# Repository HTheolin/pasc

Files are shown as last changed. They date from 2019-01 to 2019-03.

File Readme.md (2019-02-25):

# Användbara länkar

## Rust
svd2rust - https://docs.rs/svd2rust/0.14.0/svd2rust/  \
Rustboken - https://doc.rust-lang.org/1.4.0/book/README.html  \
Embedde rust - https://rust-embedded.github.io/book/intro/index.html  \
CubeMX och Rust - http://www.hashmismatch.net/pragmatic-bare-metal-rust/

## Hårdvara
STM32F401RE datasheet - https://www.st.com/resource/en/datasheet/stm32f401re.pdf

## Dokument
High Level specification - https://docs.google.com/document/d/1pT679ALJbP6M4RAu0LiHIDUVMe5iSUqeqp4-EVYOUyA/edit# \
Komponenter - https://docs.google.com/spreadsheets/d/1eK-V_FMpTHM5hmX8ijiI2q-JYo_6xdile7O38F0DbRs/edit#gid=0

# High Level Specification
Hälsoarmband som mäter puls och steg med pulsmätare och accelerometer.
Knapp som startar och återställer stegräknare. Strömspar som stänger display, sänker sampling frekvens, ... ev. efter lång tid utan knapptryck.
## Purpose (what problem it solves)
Mäta puls och känna av om pulsen blir låg/hög, varna vid dessa.
## Limitations (what problem(s) it cannot solve)
Visar endast realtid puls, yttre temperatur och steg, inget minne. Larmar endast närmaste omgivningen. 
## Behaviour (how the problem is solved)
Genom att mäta puls med en sensor en gång per sek, om den blir låg eller hög starta larm med högtalare. Visar data på display. Återställer data och startar genom knapptryck. Med detta system skapas en tryggare värld.

## Safety (what it must not do, e.g., electrocute the user)
Eftersom systemet är designat att vara i kontakt med person, måste tåla viss mängd fukt och inte ge elektiska stötar till användaren.
## Liveness (what it must eventually do, e.g., process data) 
Måste visa puls minst var 10e sekund under batteritid. 
## Robustness (how it should react to non-expected input, e.g., mal-formed packages)
Om ingen puls stäng system. 

# Gradings
## Grade 3
Pulse measurements from analog in. \
Timer that's set using buttons. \
Buzzer that sounds alarm when high pulse or timer reaching zero. \
USART for serial communication with com.
## Grade 4
Temperature measurements using analog in. \
Output to display using SPI \
Low power mode
## Grade 5
Accelerometer detecting steps, using accelerometer values or tap interrupts over I2C. \
Menu for selecting output to display and other settings.

# Group division
All - STM 32 init, Soldering \
August - ADC, Buttons, Display Layouts \
Simon - USART, Display \
Ridge - Timer, Piezo \
Henrik - Display, Acccelerometer

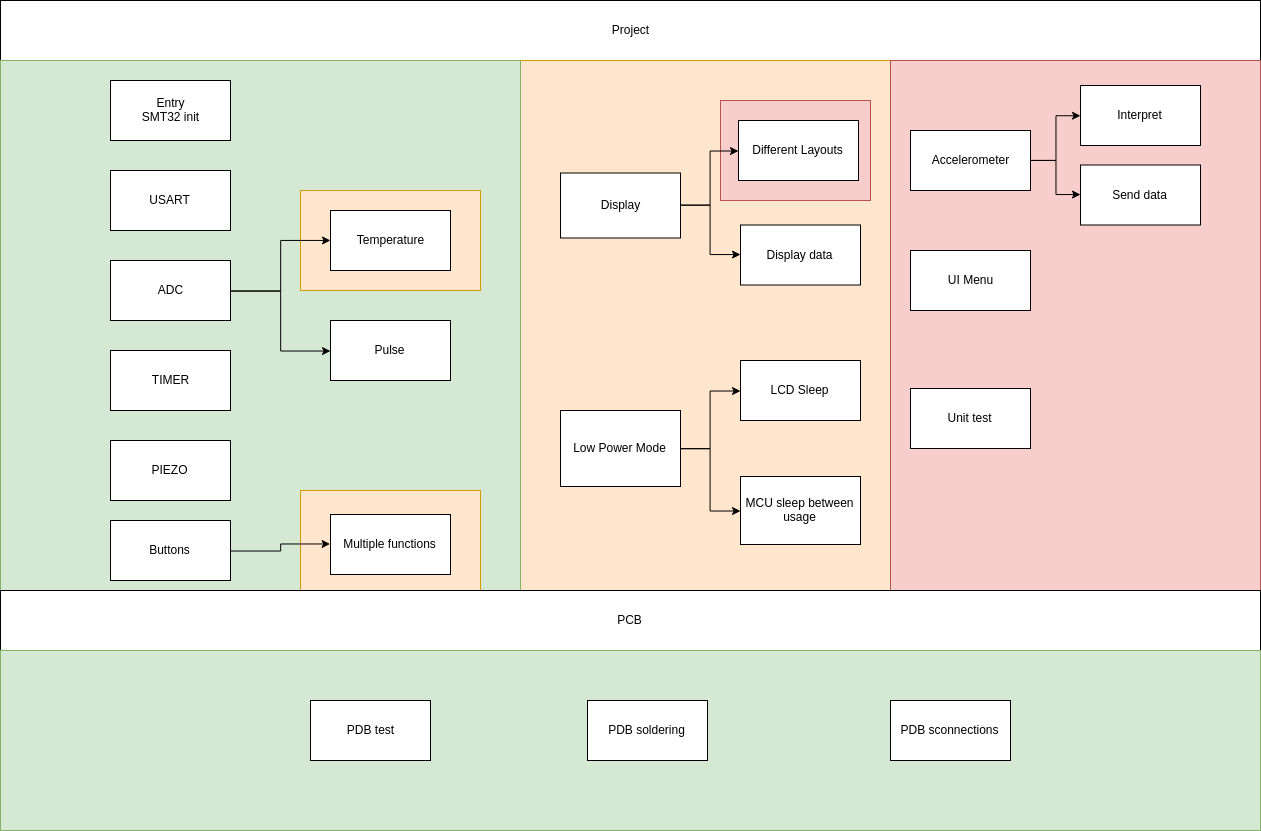
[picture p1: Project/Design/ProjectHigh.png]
System design


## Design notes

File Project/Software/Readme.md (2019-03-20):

# PASC software

## How To: Debug/Program

```
$ cargo build
$ openocd -f openocd.cfg
```

```
$ arm-none-eabi-gdb target/thumbv7em-none-eabihf/debug/Software -x openocd.gdb
```

## Difference between boards:
Layout differences between boards:

### Schematic_ons
```
    Button U9  -> MCU pin 26 (PB0)
    Button U10 -> MCU pin 27 (PB1)
    Button U11 -> MCU pin 28 (PB2)
```
LCD:
```
        3: LCD_SCE -> MCU pin 8 (PC0)
        4: LCD_RST -> MCU pin 9 (PC1)
        5: LCD_DC -> MCU pin 10 (PC2)
        6: SPI1_MOSI -> MCU pin 23 (PA7)
        7: SPI1_SCK -> MCU pin 21 (PA5)
        8: LED -> MCU pin 22 (PA6)
```

### Schematic_Ubuntu
```
    Button U9  -> MCU pin 38 (PC7)
    Button U10 -> MCU pin 39 (PC8)
    Button U11 -> MCU pin 40 (PC9)
```
LCD:
```
        3: LCD_SCE -> MCU pin 25 (PC5)
        4: LCD_RST -> MCU pin 24 (PC4)
        5: LCD_DC -> MCU pin 26 (PB0)
        6: SPI1_MOSI -> MCU pin 23 (PA7, set to SPI1_MOSI, AF05)
        7: SPI1_SCK -> MCU pin 21 (PA5, set to SPI1_SK, AF05)
        8: LED -> MCU pin 37 (PC6, set to TIM3_CH1, AF02)
```

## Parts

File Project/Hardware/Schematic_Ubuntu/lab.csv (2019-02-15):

Id | Designator | Package | Quantity | Designation | Supplier and ref
1 | SW1 | SPDT-100 | 1 | SW_SPDT
2 | U6 | Nokia5110 | 1 | Nokia5110
3 | U5 | SO-8_5.3x6.2mm_Pitch1.27mm | 1 | MAX4460ESA+
4 | BT1 | Pin_Header_Straight_1x02_Pitch2.54mm | 1 | Battery
5 | C1,C4 | CP_Radial_D5.0mm_P2.00mm | 2 | 10u
6 | C2,C3,C5,C10,C11,C12,C13,C14,C16,C17,C18 | C_0805_HandSoldering | 11 | 100n
7 | C6,C7 | C_0805_HandSoldering | 2 | 18p
8 | C8,C9 | C_0805_HandSoldering | 2 | 4.7u
9 | C15,C19 | C_0805_HandSoldering | 2 | 1u
10 | D1 | D_DO-35_SOD27_P7.62mm_Horizontal | 1 | 1N4148
11 | J1 | USB_Micro_B_Female_10118193-0001LF | 1 | USB_B_Micro
12 | J2 | Pin_Header_Straight_1x06_Pitch2.54mm | 1 | 6P Male
13 | J3 | Pin_Header_Straight_1x03_Pitch2.54mm | 1 | Conn_01x03_Male
14 | Q1 | TO-92_Inline_Wide | 1 | 2N3904
15 | R1,R2 | R_0805_HandSoldering | 2 | 10k
16 | R3,R4 | R_0805_HandSoldering | 2 | 8.2k
17 | R5,R6 | R_0805_HandSoldering | 2 | 270k
18 | R7,R13,R14,R15,R16,R17,R18 | R_0805_HandSoldering | 7 | 1k
19 | R8 | R_0805_HandSoldering | 1 | 1.8k
20 | R9,R19 | R_0805_HandSoldering | 2 | 100k
21 | R10 | R_0805_HandSoldering | 1 | 2.7k
22 | R11 | R_0805_HandSoldering | 1 | 820
23 | R12 | R_0805_HandSoldering | 1 | 330
24 | TH1 | TO-92-2pin_Inline_Narrow_Oval | 1 | PT1000
25 | U1 | SOT-223-3_TabPin2 | 1 | NCP1117-3.3_SOT223
26 | U2 | LQFP-64_10x10mm_Pitch0.5mm | 1 | STM32F411RETx
27 | U3 | LIS3DH | 1 | lis3dh_board
28 | U4 | Pin_Header_Straight_1x03_Pitch2.54mm | 1 | Pulse_sensor
29 | U7 | Piezo | 1 | piezo
30 | U8,U9,U10,U11 | Momentswitch | 4 | MomentSwitch
31 | Y1 | Crystal_SMD_HC49-SD_HandSoldering | 1 | 8MHz
32 | C20,C21,C22 | C_0805_HandSoldering | 3 | C

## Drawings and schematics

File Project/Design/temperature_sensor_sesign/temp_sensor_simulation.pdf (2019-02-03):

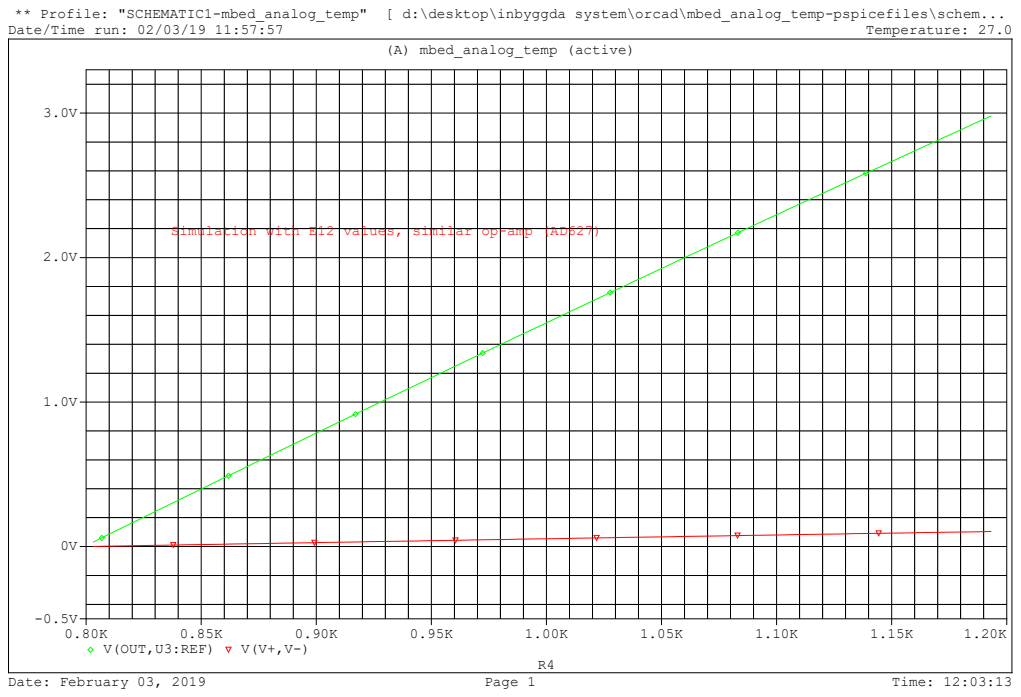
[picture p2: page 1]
Temperature: 27.0; Date: February 03, 2019; Page 1; Time: 12:03:13; (A) mbed_analog_temp (active); V(OUT,U3:REF); Simulation with E12; values,; similar; op-amp (AD627)

** Profile: "SCHEMATIC1-mbed_analog_temp" [ d:\desktop\inbyggda system\orcad\mbed_analog_temp-pspicefiles\schem...
Date/Time run: 02/03/19 11:57:57

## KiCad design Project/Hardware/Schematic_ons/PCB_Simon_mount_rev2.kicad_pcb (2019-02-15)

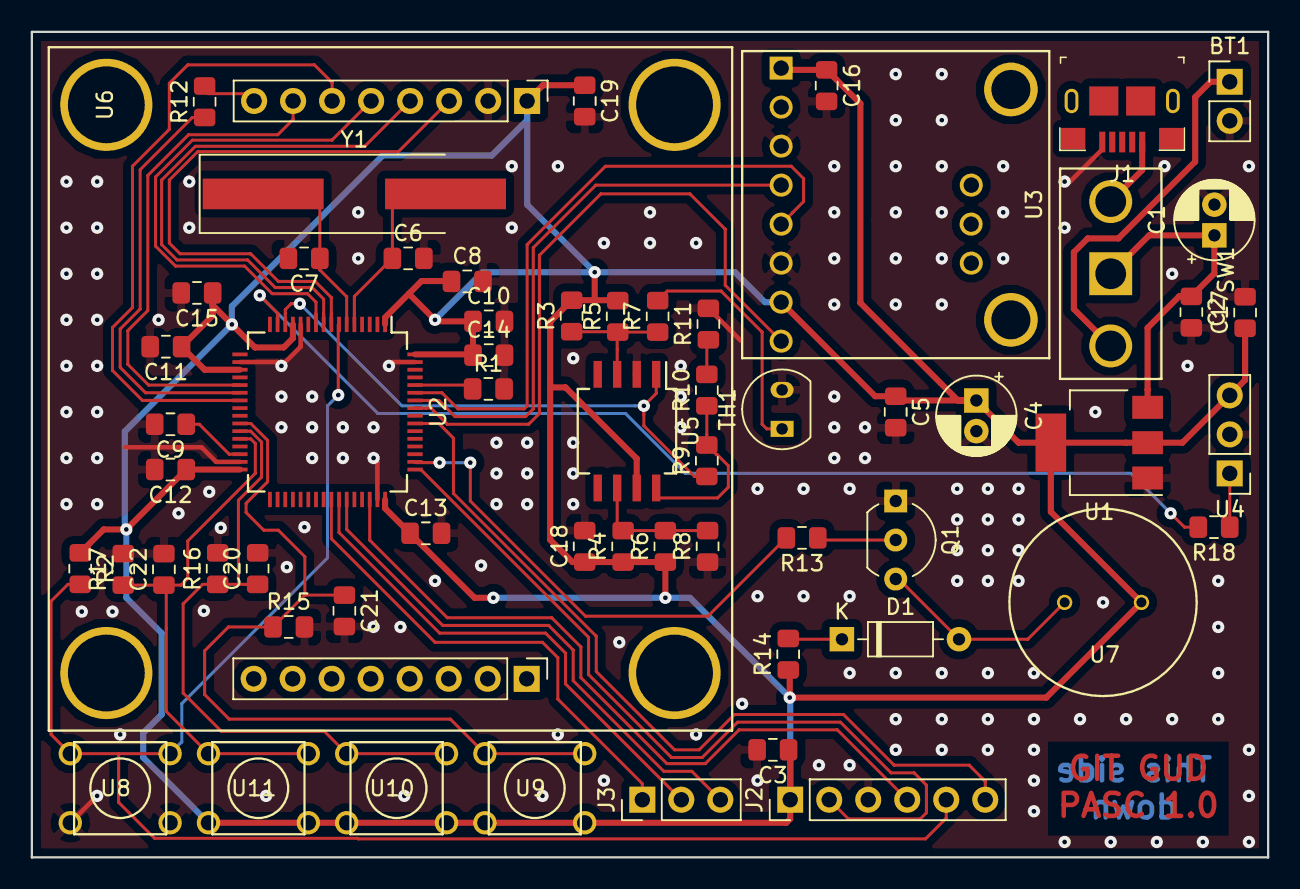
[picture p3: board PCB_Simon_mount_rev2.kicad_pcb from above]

Board: 2 copper layers, 80.5 x 53.8 mm, 60 parts (0 on the bottom side), 41 nets.

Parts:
BT1: Battery; PinHeader_1x02_P2.54mm_Vertical
C1, C4: 10u; CP_Radial_D5.0mm_P2.00mm
C2, C3, C5, C10, C11, C12, C13, C14, C16, C17, C18, C20, C21, C22: 100n; C_0805_2012Metric_Pad1.15x1.40mm_HandSolder
C6, C7: 18p; C_0805_2012Metric_Pad1.15x1.40mm_HandSolder
C8, C9: 4.7u; C_0805_2012Metric_Pad1.15x1.40mm_HandSolder
C15, C19: 1u; C_0805_2012Metric_Pad1.15x1.40mm_HandSolder
D1: 1N4148; D_DO-35_SOD27_P7.62mm_Horizontal
J1: USB_B_Micro; USB_Micro_B_Female_10118193-0001LF
J2: 6P Male; PinHeader_1x06_P2.54mm_Vertical
J3: Conn_01x03_Male; PinHeader_1x03_P2.54mm_Vertical
Q1: 2N3904; TO-92_Inline_Wide
R1, R2: 10k; R_0805_2012Metric_Pad1.15x1.40mm_HandSolder
R3, R4: 8.2k; R_0805_2012Metric_Pad1.15x1.40mm_HandSolder
R5, R6: 270k; R_0805_2012Metric_Pad1.15x1.40mm_HandSolder
R7, R13, R14, R15, R16, R17, R18: 1k; R_0805_2012Metric_Pad1.15x1.40mm_HandSolder
R8: 1.8k; R_0805_2012Metric_Pad1.15x1.40mm_HandSolder
R9: 100k; R_0805_2012Metric_Pad1.15x1.40mm_HandSolder
R10: 2.7k; R_0805_2012Metric_Pad1.15x1.40mm_HandSolder
R11: 820; R_0805_2012Metric_Pad1.15x1.40mm_HandSolder
R12: 330; R_0805_2012Metric_Pad1.15x1.40mm_HandSolder
SW1: SW_SPDT; SPDT-100
TH1: PT1000; TO-92-2
U1: NCP1117-3.3_SOT223; SOT-223-3_TabPin2
U2: STM32F411RETx; LQFP-64_10x10mm_P0.5mm
U3: lis3dh_board; LIS3DH
U4: Pulse_sensor; PinHeader_1x03_P2.54mm_Vertical
U5: MAX4460ESA+; SO-8_5.3x6.2mm_P1.27mm
U6: Nokia5110
U7: piezo; Piezo
U8, U9, U10, U11: MomentSwitch; Momentswitch
Y1: 8MHz; Crystal_SMD_HC49-SD_HandSoldering

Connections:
+3V3: C3.1, C4.1, C5.1, C8.1, C10.1, C11.1, C12.1, C13.1, C14.1, C15.1, C16.1, C17.1, C18.1, C19.1, J2.1, R2.1, R3.2, R4.1, R5.2, R6.1, R14.1, U1.2, U2.1, U2.13, U2.19, U2.32, U2.48, U2.64, U3.1, U3.7, U4.3, U5.7, U6.1, U7.1, U9.1, U9.2, U10.1, U10.2, U11.1, U11.2
+5V: J1.1, SW1.3
+BATT: BT1.1, SW1.1
+VIN: C1.1, C2.1, SW1.2, U1.3
/CS_INT: U2.57, U3.8
/Display/LED: R12.2, U6.8
/I2C1_SCL: U2.58, U3.4
/I2C1_SDA: U2.59, U3.5
/LCD_DC: U2.10, U6.5
/LCD_RST: U2.9, U6.4
/LCD_SCE: U2.8, U6.3
/NRST: J2.5, R2.2, U2.7, U8.3, U8.4
/PIEZOPWM: R13.2, U2.50
/PULSESIG: R18.2, U2.15
/SPI1_MOSI: U2.23, U6.6
/SPI1_SCK: U2.21, U6.7
/SWCLK: J2.2, U2.49
/SWDIO: J2.4, U2.46
/SWO: J2.6, U2.55
/TEMPOUT: R9.1, U2.14, U5.1
/TIM3_CH1: R12.1, U2.22
/TIM_INC: C20.1, R16.1, U2.27, U10.3, U10.4
/TIM_RES: C22.1, R17.1, U2.28, U11.3, U11.4
/TIM_START: C21.1, R15.1, U2.26, U9.3, U9.4
/Temp Sensor/INAMPFB: R9.2, R10.1, U5.8
/Temp Sensor/WBRIDGE+: R3.1, R5.1, R7.1, U5.3
/Temp Sensor/WBRIDGE-: R4.2, R6.2, R8.2, U5.6
/USART1_CK: J3.1, U2.41
/USART1_RX: J3.3, U2.43
/USART1_TX: J3.2, U2.42
/XTAL+: C6.1, U2.5, Y1.2
/XTAL-: C7.1, U2.6, Y1.1
GND: BT1.2, C1.2, C2.2, C3.2, C4.2, C5.2, C6.2, C7.2, C8.2, C9.2, C10.2, C11.2, C12.2, C13.2, C14.2, C15.2, C16.2, C17.2, C18.2, C19.2, C20.2, C21.2, C22.2, J1.5, J2.3, Q1.1, R1.2, R8.1, R11.2, R15.2, R16.2, R17.2, TH1.2, U1.1, U2.12, U2.18, U2.31, U2.47, U2.63, U3.3, U3.6, U4.2, U5.2, U6.2, U8.1, U8.2
unnamed: C9.1, U2.30
unnamed: D1.1, R14.2
unnamed: D1.2, Q1.3, U7.2
unnamed: Q1.2, R13.1
unnamed: R1.1, U2.60
unnamed: R7.2, TH1.1
unnamed: R10.2, R11.1
unnamed: R18.1, U4.1

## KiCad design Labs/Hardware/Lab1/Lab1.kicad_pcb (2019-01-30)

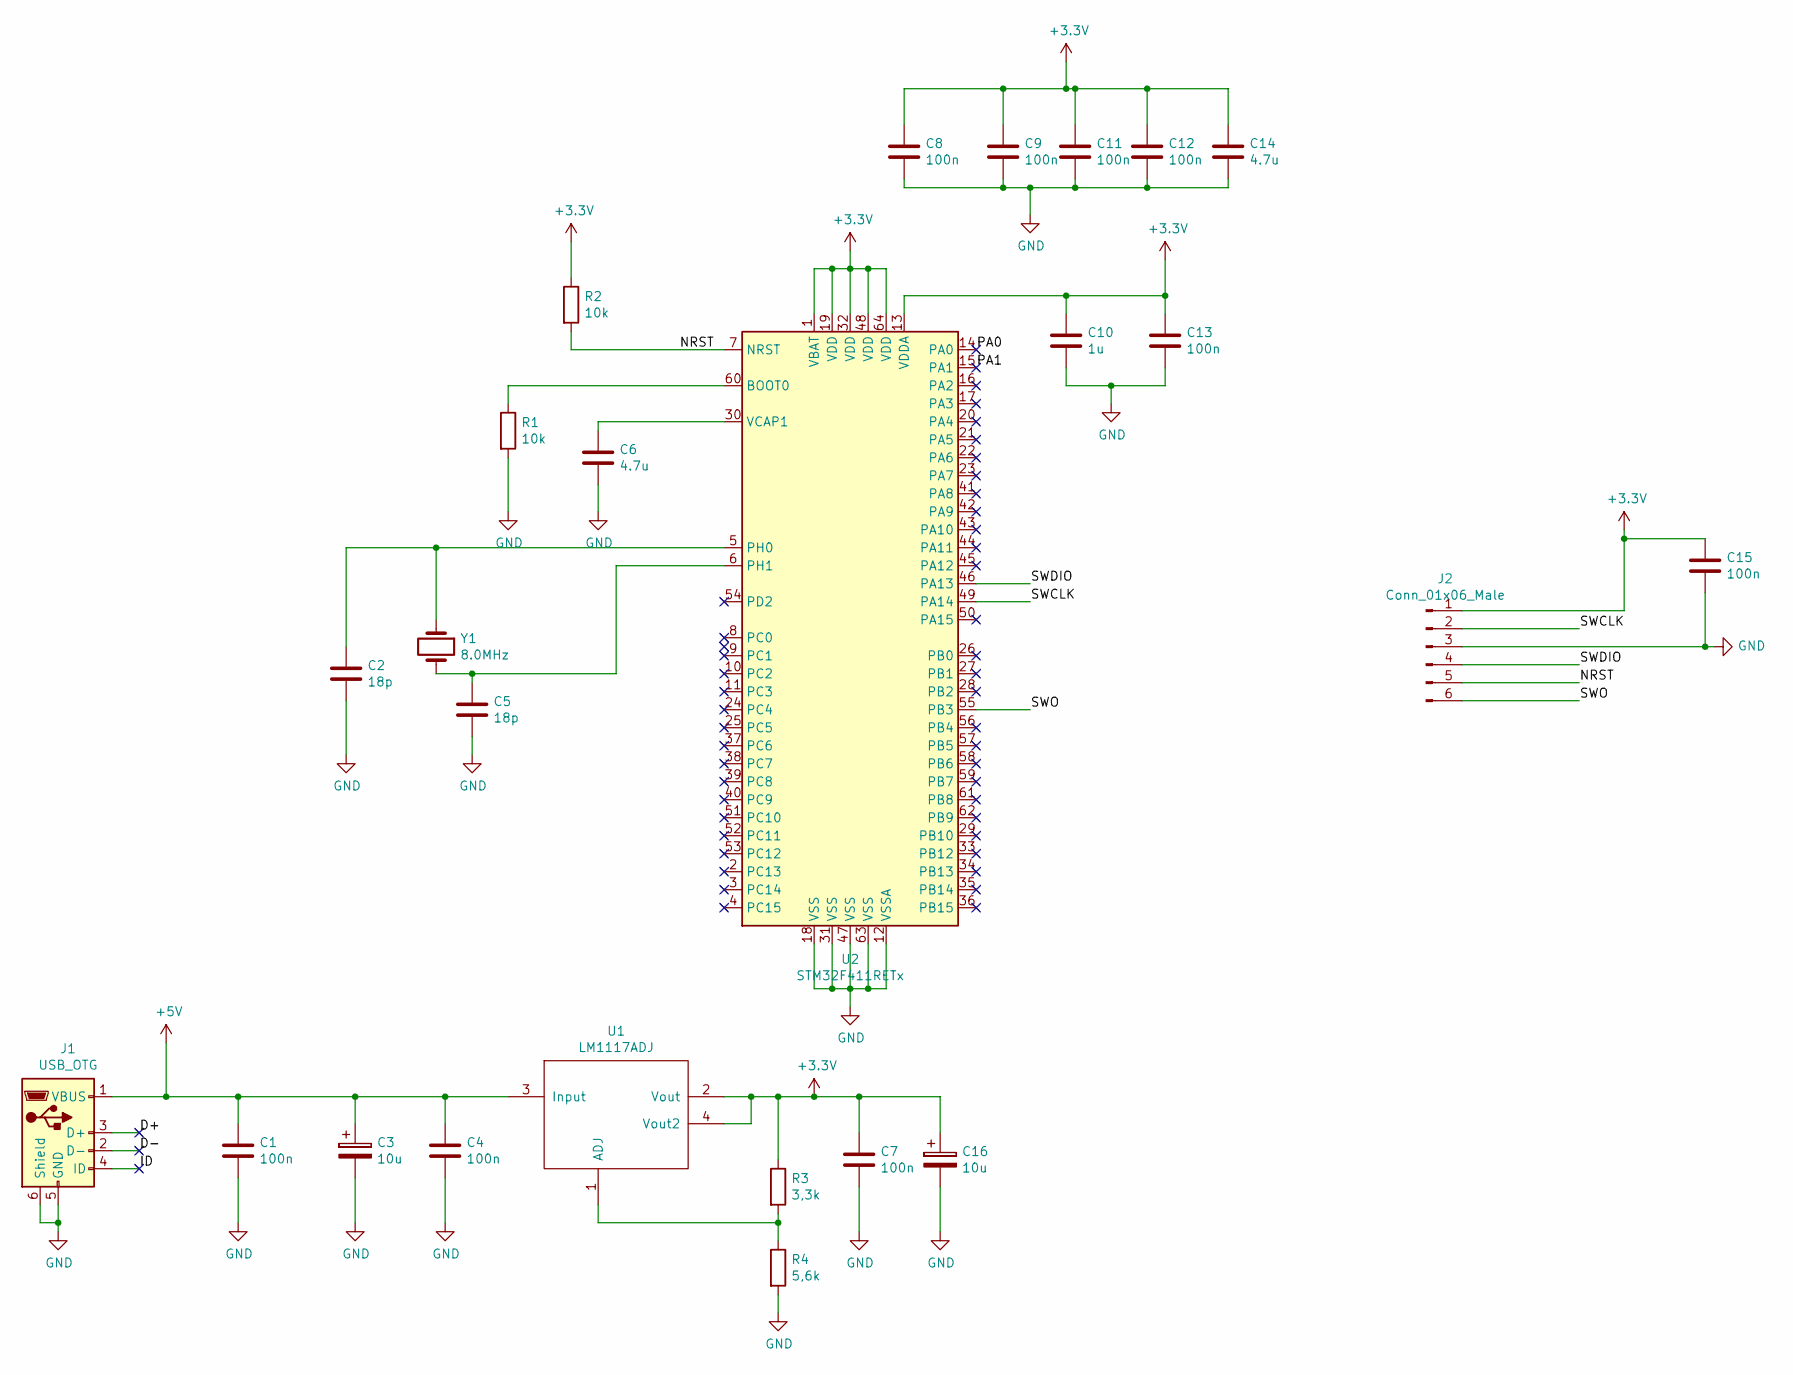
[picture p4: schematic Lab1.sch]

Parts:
C1, C4, C7, C8, C9, C11, C12, C13, C15: 100n; C_0805_HandSoldering
C2, C5: 18p; C_0805_HandSoldering
C3, C16: 10u; CP_Elec_5x5.3
C6, C14: 4.7u; C_0805_HandSoldering
C10: 1u; C_0805_HandSoldering
J1: USB_OTG; USB_Mini-B_AdamTech_MUSB-B5-S-VT-TSMT-1_SMD_Vertical
J2: Conn_01x06_Male; Pin_Header_Straight_1x06_Pitch2.54mm
R1, R2: 10k; R_0805_HandSoldering
R3: 3,3k; R_0805_HandSoldering
R4: 5,6k; R_0805_HandSoldering
U1: LM1117ADJ; SOT-223
U2: STM32F411RETx; LQFP-64_10x10mm_Pitch0.5mm
Y1: 8.0MHz; Crystal_SMD_HC49-SD_HandSoldering

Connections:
+3V3: C7.1, C8.1, C9.1, C10.1, C11.1, C12.1, C13.1, C14.1, C15.1, C16.1, J2.1, R2.1, R3.1, U1.2 (Vout), U1.4 (Vout2), U2.1 (VBAT), U2.13 (VDDA), U2.19 (VDD), U2.32 (VDD), U2.48 (VDD), U2.64 (VDD)
+5V: C1.1, C3.1, C4.1, J1.1 (VBUS), U1.3 (Input)
/D+: J1.3 (D+)
/D-: J1.2 (D-)
/ID: J1.4 (ID)
/NRST: J2.5, R2.2, U2.7 (NRST)
/PA0: U2.14 (PA0)
/PA1: U2.15 (PA1)
/SWCLK: J2.2, U2.49 (PA14)
/SWDIO: J2.4, U2.46 (PA13)
/SWO: J2.6, U2.55 (PB3)
GND: C1.2, C2.2, C3.2, C4.2, C5.2, C6.2, C7.2, C8.2, C9.2, C10.2, C11.2, C12.2, C13.2, C14.2, C15.2, C16.2, J1.5 (GND), J1.6 (Shield), J2.3, R1.2, R4.2, U2.12 (VSSA), U2.18 (VSS), U2.31 (VSS), U2.47 (VSS), U2.63 (VSS)
unnamed: C2.1, U2.5 (PH0), Y1.1
unnamed: C5.1, U2.6 (PH1), Y1.2
unnamed: C6.1, U2.30 (VCAP1)
unnamed: R1.1, U2.60 (BOOT0)
unnamed: R3.2, R4.1, U1.1 (ADJ)

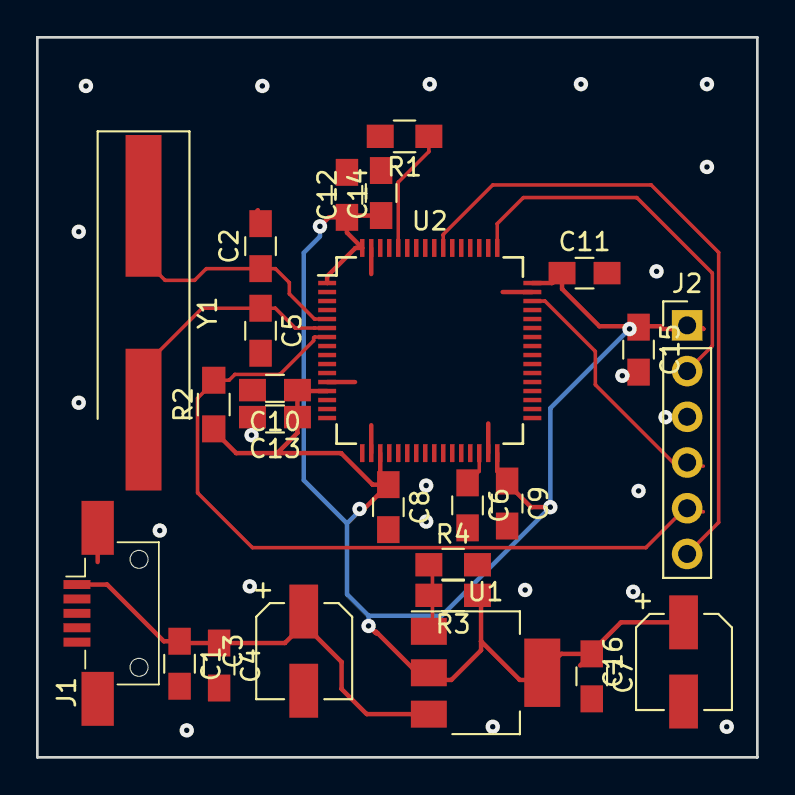
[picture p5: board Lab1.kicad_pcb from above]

Board: 2 copper layers, 40.0 x 40.0 mm, 25 parts (0 on the bottom side), 12 nets.

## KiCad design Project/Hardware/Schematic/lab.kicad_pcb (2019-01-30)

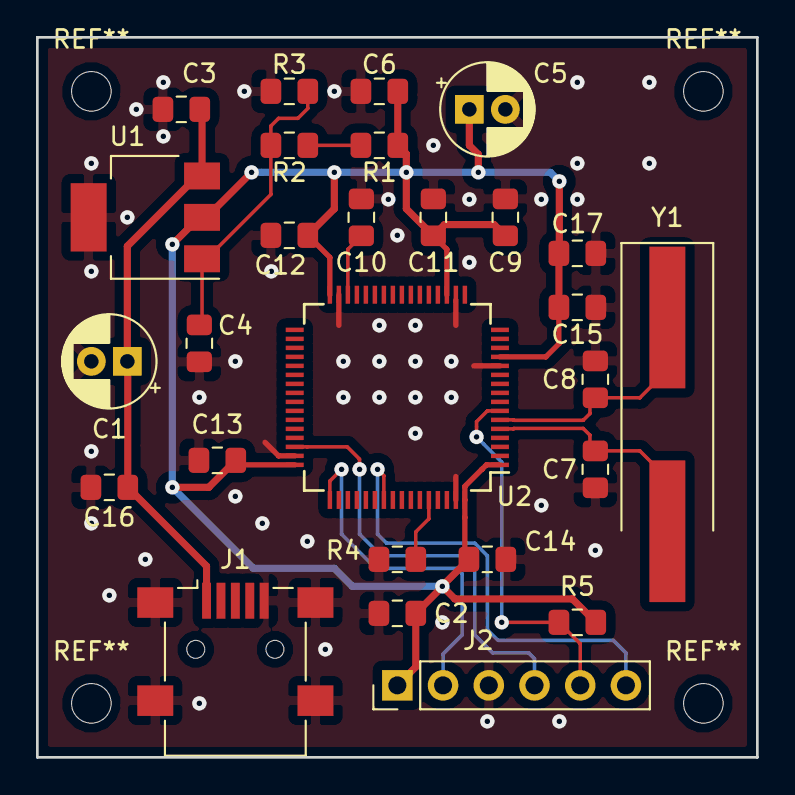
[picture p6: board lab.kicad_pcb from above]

Board: 2 copper layers, 40.0 x 40.0 mm, 27 parts (0 on the bottom side), 13 nets.

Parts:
C1, C5: 10u; CP_Radial_D5.0mm_P2.00mm
C2, C3, C4, C6, C11, C12, C13, C14, C15, C16: 100n; C_0805_2012Metric_Pad1.15x1.40mm_HandSolder
C7, C8: 18p; C_0805_2012Metric_Pad1.15x1.40mm_HandSolder
C9, C10: 4.7u; C_0805_2012Metric_Pad1.15x1.40mm_HandSolder
C17: 1u; C_0805_2012Metric_Pad1.15x1.40mm_HandSolder
J1: USB_OTG; USB_Mini-B_Lumberg_2486_01_Horizontal
J2: 6P Male; PinHeader_1x06_P2.54mm_Vertical
R1: 2.2k; R_0805_2012Metric_Pad1.15x1.40mm_HandSolder
R2: 3.9k; R_0805_2012Metric_Pad1.15x1.40mm_HandSolder
R3, R4, R5: 10k; R_0805_2012Metric_Pad1.15x1.40mm_HandSolder
U1: LM1117ADJ; SOT-223
U2: STM32F411RETx; LQFP-64_10x10mm_P0.5mm
Y1: 8MHz; Crystal_SMD_HC49-SD_HandSoldering

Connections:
+3V3: C2.1, C5.1, C6.1, C9.1, C11.1, C12.1, C13.1, C14.1, C15.1, C17.1, J2.1, R1.1, R5.1, U1.2, U2.1, U2.13, U2.19, U2.32, U2.48, U2.64
+5V: C1.1, C3.1, C16.1, J1.1, U1.3
/NRST: J2.5, R5.2, U2.7
/SWCLK: J2.2, U2.49
/SWDIO: J2.4, U2.46
/SWO: J2.6, U2.55
/XTAL+: C7.1, U2.5, Y1.2
/XTAL-: C8.1, U2.6, Y1.1
GND: C1.2, C2.2, C3.2, C4.2, C5.2, C6.2, C7.2, C8.2, C9.2, C10.2, C11.2, C12.2, C13.2, C14.2, C15.2, C16.2, C17.2, J1.5, J1.6, J2.3, R3.2, R4.2, U1.4, U2.12, U2.18, U2.31, U2.47, U2.63
unnamed: C4.1, R2.2, R3.1, U1.1
unnamed: C10.1, U2.30
unnamed: R1.2, R2.1
unnamed: R4.1, U2.60

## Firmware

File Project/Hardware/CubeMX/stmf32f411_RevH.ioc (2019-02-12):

#MicroXplorer Configuration settings - do not modify
ADC1.Channel-0\#ChannelRegularConversion=ADC_CHANNEL_1
ADC1.IPParameters=Rank-0\#ChannelRegularConversion,Channel-0\#ChannelRegularConversion,SamplingTime-0\#ChannelRegularConversion,NbrOfConversionFlag,master
ADC1.NbrOfConversionFlag=1
ADC1.Rank-0\#ChannelRegularConversion=1
ADC1.SamplingTime-0\#ChannelRegularConversion=ADC_SAMPLETIME_3CYCLES
ADC1.master=1
File.Version=6
KeepUserPlacement=false
Mcu.Family=STM32F4
Mcu.IP0=ADC1
Mcu.IP1=I2C1
Mcu.IP2=NVIC
Mcu.IP3=RCC
Mcu.IP4=SPI1
Mcu.IP5=SYS
Mcu.IP6=TIM2
Mcu.IP7=TIM3
Mcu.IP8=USART1
Mcu.IPNb=9
Mcu.Name=STM32F411R(C-E)Tx
Mcu.Package=LQFP64
Mcu.Pin0=PC0
Mcu.Pin1=PC1
Mcu.Pin10=PA10
Mcu.Pin11=PA13
Mcu.Pin12=PA14
Mcu.Pin13=PA15
Mcu.Pin14=PC10
Mcu.Pin15=PC11
Mcu.Pin16=PB3
Mcu.Pin17=PB5
Mcu.Pin18=PB6
Mcu.Pin19=PB7
Mcu.Pin2=PC2
Mcu.Pin20=VP_SYS_VS_Systick
Mcu.Pin21=VP_TIM2_VS_ClockSourceINT
Mcu.Pin3=PA0-WKUP
Mcu.Pin4=PA1
Mcu.Pin5=PA5
Mcu.Pin6=PA6
Mcu.Pin7=PA7
Mcu.Pin8=PA8
Mcu.Pin9=PA9
Mcu.PinsNb=22
Mcu.ThirdPartyNb=0
Mcu.UserConstants=
Mcu.UserName=STM32F411RETx
MxCube.Version=4.24.0
MxDb.Version=DB.4.0.240
NVIC.BusFault_IRQn=true\:0\:0\:false\:false\:true\:false
NVIC.DebugMonitor_IRQn=true\:0\:0\:false\:false\:true\:false
NVIC.HardFault_IRQn=true\:0\:0\:false\:false\:true\:false
NVIC.MemoryManagement_IRQn=true\:0\:0\:false\:false\:true\:false
NVIC.NonMaskableInt_IRQn=true\:0\:0\:false\:false\:true\:false
NVIC.PendSV_IRQn=true\:0\:0\:false\:false\:true\:false
NVIC.PriorityGroup=NVIC_PRIORITYGROUP_4
NVIC.SVCall_IRQn=true\:0\:0\:false\:false\:true\:false
NVIC.SysTick_IRQn=true\:0\:0\:false\:false\:true\:false
NVIC.UsageFault_IRQn=true\:0\:0\:false\:false\:true\:false
PA0-WKUP.Signal=ADCx_IN0
PA1.Signal=ADCx_IN1
PA10.Mode=Synchronous
PA10.Signal=USART1_RX
PA13.Locked=true
PA13.Signal=SYS_JTMS-SWDIO
PA14.Locked=true
PA14.Signal=SYS_JTCK-SWCLK
PA15.Signal=S_TIM2_CH1_ETR
PA5.Mode=Simplex_Bidirectional_Master
PA5.Signal=SPI1_SCK
PA6.Signal=S_TIM3_CH1
PA7.Mode=Simplex_Bidirectional_Master
PA7.Signal=SPI1_MOSI
PA8.Mode=Synchronous
PA8.Signal=USART1_CK
PA9.Mode=Synchronous
PA9.Signal=USART1_TX
PB3.Locked=true
PB3.Signal=SYS_JTDO-SWO
PB5.Locked=true
PB5.Signal=GPXTI5
PB6.Mode=I2C
PB6.Signal=I2C1_SCL
PB7.Mode=I2C
PB7.Signal=I2C1_SDA
PC0.Locked=true
PC0.Signal=GPIO_Output
PC1.Locked=true
PC1.Signal=GPIO_Output
PC10.Locked=true
PC10.Signal=GPIO_Output
PC11.Locked=true
PC11.Signal=GPIO_Output
PC2.Locked=true
PC2.Signal=GPIO_Output
PCC.Checker=false
PCC.Line=STM32F411
PCC.MCU=STM32F411R(C-E)Tx
PCC.PartNumber=STM32F411RETx
PCC.Seq0=0
PCC.Series=STM32F4
PCC.Temperature=25
PCC.Vdd=null
PinOutPanel.RotationAngle=0
RCC.AHBFreq_Value=16000000
RCC.APB1Freq_Value=16000000
RCC.APB2Freq_Value=16000000
RCC.CortexFreq_Value=16000000
RCC.FamilyName=M
RCC.HSE_VALUE=25000000
RCC.HSI_VALUE=16000000
RCC.I2SClocksFreq_Value=96000000
RCC.IPParameters=AHBFreq_Value,APB1Freq_Value,APB2Freq_Value,CortexFreq_Value,FamilyName,HSE_VALUE,HSI_VALUE,I2SClocksFreq_Value,LSE_VALUE,LSI_VALUE,PLLCLKFreq_Value,PLLQCLKFreq_Value,RTCFreq_Value,RTCHSEDivFreq_Value,SYSCLKFreq_VALUE,VCOI2SOutputFreq_Value,VCOInputFreq_Value,VCOInputMFreq_Value,VCOOutputFreq_Value,VcooutputI2S
RCC.LSE_VALUE=32768
RCC.LSI_VALUE=32000
RCC.PLLCLKFreq_Value=96000000
RCC.PLLQCLKFreq_Value=48000000
RCC.RTCFreq_Value=32000
RCC.RTCHSEDivFreq_Value=12500000
RCC.SYSCLKFreq_VALUE=16000000
RCC.VCOI2SOutputFreq_Value=192000000
RCC.VCOInputFreq_Value=1000000
RCC.VCOInputMFreq_Value=1000000
RCC.VCOOutputFreq_Value=192000000
RCC.VcooutputI2S=96000000
SH.ADCx_IN0.0=ADC1_IN0,IN0
SH.ADCx_IN0.ConfNb=1
SH.ADCx_IN1.0=ADC1_IN1,IN1
SH.ADCx_IN1.ConfNb=1
SH.GPXTI5.0=GPIO_EXTI5
SH.GPXTI5.ConfNb=1
SH.S_TIM2_CH1_ETR.0=TIM2_CH1,PWM Generation1 CH1
SH.S_TIM2_CH1_ETR.ConfNb=1
SH.S_TIM3_CH1.0=TIM3_CH1,Output Compare1 CH1
SH.S_TIM3_CH1.ConfNb=1
SPI1.CalculateBaudRate=8.0 MBits/s
SPI1.Direction=SPI_DIRECTION_1LINE
SPI1.IPParameters=VirtualType,Mode,Direction,CalculateBaudRate
SPI1.Mode=SPI_MODE_MASTER
SPI1.VirtualType=VM_MASTER
TIM2.Channel-PWM\ Generation1\ CH1=TIM_CHANNEL_1
TIM2.IPParameters=Channel-PWM Generation1 CH1
TIM3.Channel-Output\ Compare1\ CH1=TIM_CHANNEL_1
TIM3.IPParameters=Channel-Output Compare1 CH1
USART1.IPParameters=VirtualMode
USART1.VirtualMode=VM_SYNC
VP_SYS_VS_Systick.Mode=SysTick
VP_SYS_VS_Systick.Signal=SYS_VS_Systick
VP_TIM2_VS_ClockSourceINT.Mode=Internal
VP_TIM2_VS_ClockSourceINT.Signal=TIM2_VS_ClockSourceINT

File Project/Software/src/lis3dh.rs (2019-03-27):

extern crate embedded_hal;

use nb;
use hal::stm32::{I2C1, GPIOB, RCC};
use cortex_m::{asm};

use crate::frequency::*;
use crate::time::*;

pub const ADDRESS: u8 = 0x18;

pub const LIS3DH_REG_STATUS1: u8 = 0x07;
pub const LIS3DH_REG_OUTADC1_L: u8 = 0x08;
pub const LIS3DH_REG_OUTADC1_H: u8 = 0x09;
pub const LIS3DH_REG_OUTADC2_L: u8 = 0x0A;
pub const LIS3DH_REG_OUTADC2_H: u8 = 0x0B;
pub const LIS3DH_REG_OUTADC3_L: u8 = 0x0C;
pub const LIS3DH_REG_OUTADC3_H: u8 = 0x0D;
pub const LIS3DH_REG_INTCOUNT: u8 = 0x0E;
pub const LIS3DH_REG_WHOAMI: u8 = 0x0F;
pub const LIS3DH_REG_TEMPCFG: u8 = 0x1F;
pub const LIS3DH_REG_CTRL1: u8 = 0x20;
pub const LIS3DH_REG_CTRL2: u8 = 0x21;
pub const LIS3DH_REG_CTRL3: u8 = 0x22;
pub const LIS3DH_REG_CTRL4: u8 = 0x23;
pub const LIS3DH_REG_CTRL5: u8 = 0x24;
pub const LIS3DH_REG_CTRL6: u8 = 0x25;
pub const LIS3DH_REG_REFERENCE: u8 = 0x26;
pub const LIS3DH_REG_STATUS2: u8 = 0x27;
pub const LIS3DH_REG_OUT_X_L: u8 = 0x28;
pub const LIS3DH_REG_OUT_X_H: u8 = 0x29;
pub const LIS3DH_REG_OUT_Y_L: u8 = 0x2A;
pub const LIS3DH_REG_OUT_Y_H: u8 = 0x2B;
pub const LIS3DH_REG_OUT_Z_L: u8 = 0x2C;
pub const LIS3DH_REG_OUT_Z_H: u8 = 0x2D;
pub const LIS3DH_REG_FIFOCTRL: u8 = 0x2E;
pub const LIS3DH_REG_FIFOSRC: u8 = 0x2F;
pub const LIS3DH_REG_INT1CFG: u8 = 0x30;
pub const LIS3DH_REG_INT1SRC: u8 = 0x31;
pub const LIS3DH_REG_INT1THS: u8 = 0x32;
pub const LIS3DH_REG_INT1DUR: u8 = 0x33;
pub const LIS3DH_REG_CLICKCFG: u8 = 0x38;
pub const LIS3DH_REG_CLICKSRC: u8 = 0x39;
pub const LIS3DH_REG_CLICKTHS: u8 = 0x3A;
pub const LIS3DH_REG_TIMELIMIT: u8 = 0x3B;
pub const LIS3DH_REG_TIMELATENCY: u8 = 0x3C;
pub const LIS3DH_REG_TIMEWINDOW: u8 = 0x3D;
pub const LIS3DH_REG_ACTTHS: u8 = 0x3E;
pub const LIS3DH_REG_ACTDUR: u8 = 0x3F;

pub const Z_OFFSET: f32 = 1.0;
pub const GRAVITY_EARTH: f32 = 9.80665;
pub enum Range
{
  LIS3DH_RANGE_16_G         = 0b11,   // +/- 16g
  LIS3DH_RANGE_8_G           = 0b10,   // +/- 8g
  LIS3DH_RANGE_4_G           = 0b01,   // +/- 4g
  LIS3DH_RANGE_2_G           = 0b00    // +/- 2g (default value)
}

pub enum Divider
{
    DIV_16_G = 1365,
    DIV_8_G = 4096,
    DIV_4_G = 8190,
    DIV_2_G = 16380
}

pub enum Axis
{
  LIS3DH_AXIS_X         = 0x0,
  LIS3DH_AXIS_Y         = 0x1,
  LIS3DH_AXIS_Z         = 0x2,
}

/* Used with register 0x2A (LIS3DH_REG_CTRL_REG1) to set bandwidth */
pub enum Datarate
{
  LIS3DH_DATARATE_400_HZ     = 0b0111, //  400Hz 
  LIS3DH_DATARATE_200_HZ     = 0b0110, //  200Hz
  LIS3DH_DATARATE_100_HZ     = 0b0101, //  100Hz
  LIS3DH_DATARATE_50_HZ      = 0b0100, //   50Hz
  LIS3DH_DATARATE_25_HZ      = 0b0011, //   25Hz
  LIS3DH_DATARATE_10_HZ      = 0b0010, // 10 Hz
  LIS3DH_DATARATE_1_HZ       = 0b0001, // 1 Hz
  LIS3DH_DATARATE_POWERDOWN  = 0,
  LIS3DH_DATARATE_LOWPOWER_1K6HZ  = 0b1000,
  LIS3DH_DATARATE_LOWPOWER_5KHZ  =  0b1001,

}

/// I2C error
#[derive(Debug)]
pub enum I2CError {
    /// Overrun occurred
    Overrun,
    /// Timeout occurred, SCL remained LOW for 25 ms
    Timeout,
    /// Bus error
    BusError,
    #[doc(hidden)] _Extensible,
    NACK,
}

pub enum Error<E> {
    I2C(E),
}

pub struct Axis_g {
    x_g: f32,
    y_g: f32,
    z_g: f32
}

impl Axis_g {
    pub fn new() -> Self {
        Axis_g {
            x_g: 0f32,
            y_g: 0f32,
            z_g: 0f32,
        }      
    }

    pub fn x_g(&self) -> f32 {
        self.x_g
    }
    pub fn y_g(&self) -> f32 {
        self.y_g
    }
    pub fn z_g(&self) -> f32 {
        self.z_g
    }
}

pub struct Accelerometer {
    axis: Axis_g,
    range: Range,
    i2c: I2C1,
}

impl Accelerometer {
    pub fn new(i2c1: I2C1) -> Self {
        Accelerometer {
            axis: Axis_g::new(),
            range: Range::LIS3DH_RANGE_2_G,
            i2c: i2c1,
        }
    }

    /// High res & BDU enabled, DRDY on INT1
    pub fn setup(&mut self) {
        //Enable x, y, z axis 
        self.write_register(&mut [LIS3DH_REG_CTRL1, 0x07]).unwrap();
        //High res & BDU
        self.write_register(&mut [LIS3DH_REG_CTRL4, 0x88]).unwrap();
        //no DRDY on INT1
        self.write_register(&mut [LIS3DH_REG_CTRL3, 0x00]).unwrap();
        //Interrupt active high = bit 2 set low bit 2 clear 
        self.write_register(&mut [LIS3DH_REG_CTRL6, 0x02]).unwrap();

        self.write_register(&mut [LIS3DH_REG_CTRL2, 0x00]).unwrap(); // high pass filter

    }

    /// Set datarate for the accelerometer update
    pub fn set_datarate(&mut self, datarate: Datarate) {
        let mut ctl1 = [0; 1];
        self.write_read_register(LIS3DH_REG_CTRL1, &mut ctl1).unwrap();
        ctl1[0] &= !(0xF0);
        ctl1[0] |= (datarate as u8) << 4;
        self.write_register(&mut [LIS3DH_REG_CTRL1, ctl1[0]]).unwrap();
    }

    /// Sets the range of the accelerometer accurary
    pub fn set_range(&mut self, range: Range) {
        self.range = range;
        let mut r = [0; 1];
        self.write_read_register(LIS3DH_REG_CTRL4, &mut r).unwrap();
        r[0] &= !(0x30);
        let r_u8 = match self.range {
            Range::LIS3DH_RANGE_16_G => Range::LIS3DH_RANGE_16_G as u8,
            Range::LIS3DH_RANGE_8_G => Range::LIS3DH_RANGE_8_G as u8,
            Range::LIS3DH_RANGE_4_G => Range::LIS3DH_RANGE_4_G as u8,
            Range::LIS3DH_RANGE_2_G => Range::LIS3DH_RANGE_2_G as u8
        };
        r[0] |= (r_u8) << 4;
        self.write_register(&mut [LIS3DH_REG_CTRL4, r[0]]).unwrap();
    }

    /// Enable interrupt for clicks, 
    /// c nr of taps, 0 disable, 1 single, 2 double
    /// clickthreash, threashold for the interrupt to be set
    ///     this strongly depend on the range! for 16G, try 5-10
    ///     for 8G, try 10-20. for 4G try 20-40. for 2G try 40-80
    ///
    /// timelimit 
    /// timelatency latency for interrupt after click was registered
    /// timewindow How often a click interrupt is allowed
    /// 
    pub fn set_click_interrupt(&mut self, c: u8, clickthresh: u8, timelimit: u8, timelatency: u8, timewindow: u8) {
        if c == 0 {
            //disable int
            let mut r = [0; 1];
            self.write_read_register(LIS3DH_REG_CTRL3, &mut r).unwrap();
            r[0] &= !(0x80); // turn off I1_CLICK
            self.write_register(&mut [LIS3DH_REG_CTRL3, r[0]]).unwrap();
            self.write_register(&mut [LIS3DH_REG_CLICKCFG, 0]).unwrap();
            return;
        }
        // else...

        self.write_register(&mut [LIS3DH_REG_CTRL3, 0x80]).unwrap(); // turn on int1 click
        self.write_register(&mut [LIS3DH_REG_CTRL5, 0x08]).unwrap(); // latch interrupt on int1
        self.write_register(&mut [LIS3DH_REG_CTRL2, 0x94]).unwrap(); // high pass filter

        if c == 1 {
            self.write_register(&mut [LIS3DH_REG_CLICKCFG, 0x15]).unwrap(); // turn on all axes & singletap
        } else if c ==2 {
            self.write_register(&mut [LIS3DH_REG_CLICKCFG, 0x2A]).unwrap(); // turn on all axes & doubletap
        }
        self.write_register(&mut [LIS3DH_REG_CLICKTHS, clickthresh]).unwrap(); // arbitrary
        self.write_register(&mut [LIS3DH_REG_TIMELIMIT, timelimit]).unwrap(); // arbitrary
        self.write_register(&mut [LIS3DH_REG_TIMELATENCY, timelatency]).unwrap(); // arbitrary
        self.write_register(&mut [LIS3DH_REG_TIMEWINDOW, timewindow]).unwrap(); // arbitrary
    }

    /// Check device ID, should be 51.
    pub fn who_am_i(&mut self, buffer: &mut [u8]) -> Result<(), nb::Error<I2CError>> {
        enable(&self.i2c);
        while start(&self.i2c).is_err() {};
        let mut rx_buffer = [0; 2];
        while write(&self.i2c, &mut [LIS3DH_REG_WHOAMI as u8]).is_err() {}
        while start(&self.i2c).is_err() {};
        read_ack(&self.i2c, buffer);
        Ok(())
    }

    /// Writes a register address to the device then reads the resuld into a buffer
    pub fn write_read_register(&mut self, reg: u8, buffer: &mut [u8]) -> Result<(), nb::Error<I2CError>> {
        enable(&self.i2c);
        while start(&self.i2c).is_err() {};
        while write(&self.i2c, &mut [reg as u8]).is_err() {}
        while start(&self.i2c).is_err() {};
        read_ack(&self.i2c, buffer);
        Ok(())
    }

    /// Writes value from a [u8] indo the the register defined as the first element in data
    pub fn write_register(&mut self, data: &mut [u8]) -> Result<(), nb::Error<I2CError>> {
        enable(&self.i2c);
        while start(&self.i2c).is_err() {};
        while write(&self.i2c, data).is_err() {};
        while stop(&self.i2c).is_err() {};
        Ok(())
    }

    /// read values form x,y,z axis on the device, divides with value based on the range set to approximate G forces
    /// Stores values into self.axis
    pub fn read_accelerometer(&mut self, data: &mut [u8]) -> Result<(), nb::Error<I2CError>> {
        // I2Cinterface->write(LIS3DH_REG_OUT_X_L | 0x80);
        enable(&self.i2c);
        while start(&self.i2c).is_err() {};
        while write(&self.i2c, &mut [LIS3DH_REG_OUT_X_L | 0x80]).is_err() {};
        while start(&self.i2c).is_err() {};
        read_ack(&self.i2c, data);
        let divider = match self.range {
            Range::LIS3DH_RANGE_16_G => Divider::DIV_16_G as u16,
            Range::LIS3DH_RANGE_8_G => Divider::DIV_8_G as u16,
            Range::LIS3DH_RANGE_4_G => Divider::DIV_4_G as u16,
            Range::LIS3DH_RANGE_2_G => Divider::DIV_2_G as u16
        };
        let x = data[0] as i16 | (data[1] as i16) << 8;
        let y = data[2] as i16 | (data[3] as i16) << 8;
        let z = data[4] as i16 | (data[5] as i16) << 8;
        let x_g = (x as f32) / (divider as f32);
        let y_g = (y as f32) / (divider as f32);
        let z_g = (z as f32) / (divider as f32);
        self.axis.x_g = x_g * GRAVITY_EARTH;
        self.axis.y_g = y_g * GRAVITY_EARTH;
        self.axis.z_g = z_g  * GRAVITY_EARTH;
        Ok(())
    }

    pub fn get_click(&self, data: &mut [u8]) -> Result<(), nb::Error<I2CError>> {
        enable(&self.i2c);
        while start(&self.i2c).is_err() {};
        while write(&self.i2c, &mut [LIS3DH_REG_CLICKSRC]).is_err() {};
        while start(&self.i2c).is_err() {}; 
        read_ack(&self.i2c, data);
        Ok(())
    }

    pub fn clear_interrupt(&self, data: &mut [u8]) -> Result<(), nb::Error<I2CError>> {
         enable(&self.i2c);
        while start(&self.i2c).is_err() {};
        while write(&self.i2c, &mut [LIS3DH_REG_INT1SRC]).is_err() {};
        while start(&self.i2c).is_err() {}; 
        read_ack(&self.i2c, data);
        Ok(())
    }

    pub fn axis(&mut self) -> &Axis_g {
        &self.axis
    }
}
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

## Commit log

2019-01-22 Lab1 påbörjad
    [Lab1.kicad_pcb, Lab1.sch]
2019-01-29 Lab 1
    [Lab1.kicad_pcb, Lab1.sch]
2019-01-30 Lab2 med gerber
    [Lab1-B.Cu.gbr, Lab1-B.Mask.gbr, Lab1-Edge.Cuts.gbr, Lab1-F.Cu.gbr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]
2019-01-30 Första projekt KiCAD commit.
    [lab-B.Cu.gbr, lab-B.Mask.gbr, lab-Edge.Cuts.gbr, lab-F.Cu.gbr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]
2019-02-01 sensor ritning
2019-02-01 Accelerometer footprint
    [accelerometer.sch, lab.sch]
2019-02-01 Lagt till sheets för alla delar
    [accelerometer.sch, buttons.sch, display.sch, lab.sch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]
2019-02-02 Lade till krets för temperatursensor.
    [accelerometer.sch, buttons.sch, display.sch, lab.sch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]
2019-02-02 MATLAB-script för design av temperaturkrets
2019-02-03 Lade till simuleringsplot av temperatursensorkretsen.
2019-02-03 Lade till anteckningar för design av temperatursensorkretsen.
2019-02-04 Lade till komponentvärden i kretsschemat för temperatursensorkretsen
    [tempsensor.sch]
2019-02-04 Skapade LCD symbol och lade till display-krets.
    [display.sch]
2019-02-04 Lade till gate-resistor till LCD-backlight FETen.
    [display.sch]
2019-02-05 Ändrade power supply till två fixed: en 3v3 och en 5v.
    [lab.sch]
2019-02-05 Accelerometer (#1)
    * Accelerometer footprint
    * Connections till processor
    * Lagt till i2c och usart i cubemx
    [accelerometer.sch, lab.sch]
2019-02-05 La till connection stm32 till display, footprint for DEM16220 lcd (#4)
    [display.sch, lab.sch]
2019-02-06 Ändrade i display: lade till LED-kontroll, bytte plats på LED- LED+ utifrån databladet.
    [display.sch]
2019-02-07 Rätta felstavning
    [accelerometer.sch]
2019-02-07 Ändrade CS-pin på accelerometern, lade till kommentarer och värde på bypassen.
    [accelerometer.sch, lab.sch]
2019-02-08 Add files via upload (#6)
    Switches inlagda och MicroUSB
    [buttons.sch, lab.sch]
2019-02-08 Pulse, piezo och labels (#8)
    [accelerometer.sch, buttons.sch, display.sch, lab.sch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]
2019-02-08 Pin mappning i cubemx
2019-02-08 Bytte display
    [display.sch, lab.sch]
2019-02-08 Ny display, igen!
    [display.sch, lab.sch]
2019-02-08 Lade till symbol för +7V och 7-voltsregulatorn, samt kopplade in regulatorn.
    [lab.sch]
2019-02-08 Korrigerade 7-voltsregulatorn: det är fixed, inte adjustable.
    [lab.sch]
2019-02-08 Buttons och display (#9)
    [buttons.sch, display.sch]
2019-02-08 Lcd (#10)
    * La till en till display och fixa fel
    [accelerometer.sch, buttons.sch, display2.sch, lab.sch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]
2019-02-12 Byta skärm, igen igen (#11)
    [accelerometer.sch, buttons.sch, display.sch, lab.sch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]
2019-02-12 Tog bort power supply +7, lade till switch för att switcha mellan batteri och USB power. Lade till power-net symbol för oregulerad supply voltage +VIN.
    [accelerometer.sch, buttons.sch, display.sch, lab.sch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]
2019-02-12 Lcd bb (#12)
    * Tagit bort knapp, ändrat power till piezo
    [accelerometer.sch, buttons.sch, lab.sch, piezo.sch]
2019-02-13 Lade till vippströmställare footprint och uppdaterade max4460 footprint för att det förhoppningsvis ska laddas av alla
    [lab.sch, tempsensor.sch]
2019-02-15 Pcb rev1 (#13)
    * Extra resistor till temp gain, två cubemx project med olika pinsmaps, Gerber filer till pcb_revS
    * Updatera footprint för Switch samt gerber
    [accelerometer.sch, buttons.sch, display.sch, display2.sch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]
2019-02-15 Gerber, csv boom, cap till knappar
    [buttons.sch, lab-B.Cu.gbr, lab-B.Mask.gbr, lab-Edge.Cuts.gbr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]
2019-02-15 Pcb rev1 simon (#14)
    Klar PCB av Simon
    Added resistor to pulse, and capacitors to buttons
    [PCB_Simon.kicad_pcb, PCB_Simon_mount.kicad_pcb, PCB_Simon_mount_rev2.kicad_pcb, PCB_Simon_mount_rev2.sch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]
2019-02-15 Updaterat footprint samt boom
    [lab.csv]
2019-02-15 Hardware finished for ordering
    [PCB_Simon_mount_rev2-B.Cu.gbr, PCB_Simon_mount_rev2-B.Mask.gbr, PCB_Simon_mount_rev2-Edge.Cuts.gbr, PCB_Simon_mount_rev2-F.Cu.gbr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]
2019-03-13 Added both board pin layouts for buttons
2019-03-19 I2c (#19)
    * A mess of i2c
    * Working on not working i2c
    * Simplified toggle between boards, some cleanups
2019-03-20 Lade till PCBskillnader i readme och lade till LCD-datablad.
2019-03-20 LCD on Simon's PCB (SPCB) requires higher contrast than Henrik's PCB (HPCB)
2019-03-26 Pulse sensor.
2019-03-26 Pedo cont (#22)
    * fix accelerometer h l byte order, added sample arrays for max/min values
    * Fix gravity values
    * Added vector pointing down
    * Increased acc sensitivity
    * Added pin interrupt check
    * Experiment with pedometer from android
    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
2019-03-27 Pedo filtered (#23)
    * Cleanup
    * another step detector
    * Added another step
    * optimized lcd clear, filtered step counter
    * Pedometer with global world z and velocity estimate
    * ultamate pedometer
    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
2019-03-27 Swap board
2019-03-27 Pcb h (#24)
    * Added guiding for users when bad pulse data
    * img arrays
    * Redraw heart on toggle
